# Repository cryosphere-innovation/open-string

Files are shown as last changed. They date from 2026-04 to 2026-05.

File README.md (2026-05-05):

# OpenString

<!-- SPDX-License-Identifier: CC-BY-SA-4.0 -->
<!-- Copyright (c) 2026 Cryosphere Innovation (a wholly owned subsidiary of JASCO Applied Sciences). -->
<!-- Contact: Dr. Cameron Planck <cjp@cryosphereinnovation.com> -->

OpenString is the world's first open-source temperature string for environmental monitoring. It consists of a PCB design, firmware package, and assembly guide to help you bring temperature profile monitoring into any project.

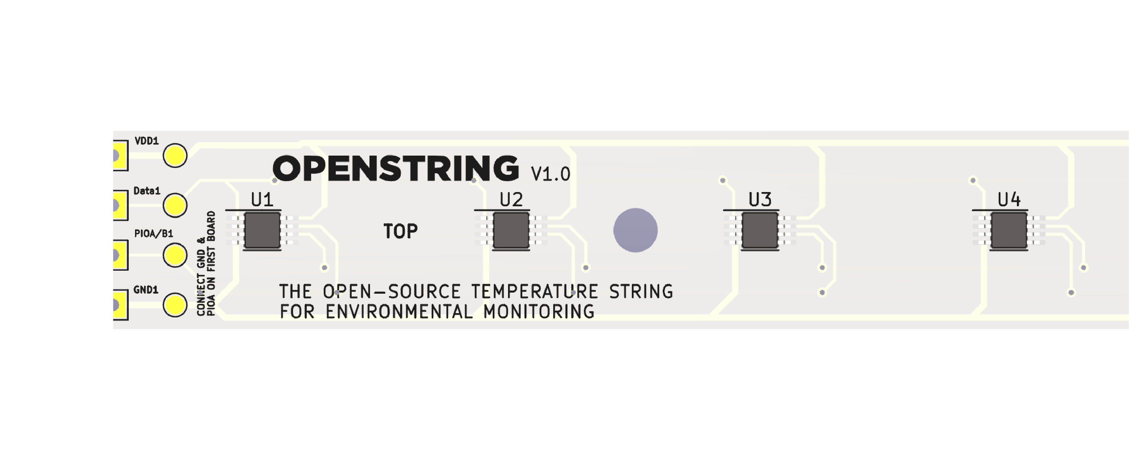
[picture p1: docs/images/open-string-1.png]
OpenString


Based on the production temperature string used by [SIMB3](https://cryosphereinnovation.com/simb3), OpenString is an extensible, arctic-hardened design that can be used as-is or tailored to your specific application. Everything you need to build, flash, and deploy one is in this repo.

> **Don't want to build your own?** Cryosphere Innovation can supply ready-to-use, assembled OpenString boards. Email [cjp@cryosphereinnovation.com](mailto:cjp@cryosphereinnovation.com) for pricing and lead time.

## Repository layout

| Path        | Contents                                                     |
| ----------- | ------------------------------------------------------------ |
| `hardware/` | KiCad project, schematic, PCB, Gerbers, BOM, fab-house notes |
| `firmware/` | Arduino sketch for the microcontroller (single `.ino` file)  |
| `docs/`     | Markdown (MDX) source rendered on the Cryosphere docs site   |
| `LICENSES/` | Full text of each license used in the project                |
| `LICENSE`   | Top-level license map                                        |

## Build your own

1. Read [`docs/ordering.mdx`](./docs/ordering.mdx) to order the PCB and parts.
2. Follow [`docs/open-string-assembly.mdx`](./docs/open-string-assembly.mdx) for the multi-step assembly walkthrough (soldering, housing, potting, testing).
3. Flash the firmware (see below, or [`docs/firmware.mdx`](./docs/firmware.mdx)).
4. Deploy.

## Hardware

The KiCad project and fabrication outputs live in `hardware/`:

- `hardware/board-files/` — KiCad project (schematic, PCB layout, project settings)
- `hardware/fabrication/gerbers/` — Gerbers and drill files ready to upload to a PCB house

See [`docs/ordering.mdx`](./docs/ordering.mdx) for the current ordering guide
(fab house settings, stencil, assembly options, expected cost).

Hardware design files are released under **CERN-OHL-S 2.0**
([`LICENSES/CERN-OHL-S-2.0.txt`](./LICENSES/CERN-OHL-S-2.0.txt)).

## Firmware

Single-file Arduino sketch at
[`firmware/src/open_string.ino`](./firmware/src/open_string.ino). PlatformIO
project config at [`platformio.ini`](./platformio.ini). Target board:
**Adafruit Feather M0** (SAMD21).

### Building with PlatformIO (recommended)

1. Install [PlatformIO Core](https://docs.platformio.org/page/core/installation.html)
   (or the PlatformIO IDE extension for VS Code).
2. From the repo root (the folder containing `platformio.ini`):
   ```sh
   pio run                  # compile
   pio run --target upload  # flash over USB
   pio device monitor       # open serial console at 115200 baud
   ```
   PlatformIO installs the SAMD board support and the OneWire library
   automatically based on `platformio.ini`.

   In VS Code, open the repo root as the workspace folder so the
   PlatformIO extension can find `platformio.ini`.

### Building with the Arduino IDE

1. Install the [Arduino IDE](https://www.arduino.cc/en/software) (or
   `arduino-cli`) and the SAMD board support package.
2. The Arduino IDE expects the sketch folder name to match the `.ino`
   filename — rename `firmware/src/` to `firmware/open_string/` (or
   symlink it) and open `open_string.ino` from there.
3. Select **Adafruit Feather M0** as the board, pick the right port,
   and click **Upload**.

See [`docs/firmware.mdx`](./docs/firmware.mdx) for the full flashing
guide, including fuse settings and troubleshooting.

Firmware source is released under **GPL-3.0**
([`LICENSES/GPL-3.0.txt`](./LICENSES/GPL-3.0.txt)).

## License

OpenString is multi-licensed. See [`LICENSE`](./LICENSE) for the full map.
Summary:

- **Hardware** — CERN-OHL-S 2.0
- **Firmware** — GPL-3.0
- **Documentation** — CC-BY-SA-4.0

All three allow commercial use and require attribution. Derivative works
must remain open under the same license.

## How the docs are published

The OpenString documentation lives at
[cryosphereinnovation.com/docs](https://cryosphereinnovation.com/docs).
The live site bakes the MDX files in `docs/` into its build output
when it deploys, so changes here go live the next time the docs site
rebuilds.

`docs/manifest.json` is generated automatically by a GitHub Action
(`.github/workflows/manifest.yml`) on every push that touches an MDX
file. You don't need to edit it by hand — just add/edit `.mdx` files
and push.

## Contributing

Issues and pull requests welcome. By contributing, you agree to license
your contribution under the license that applies to the directory you
are contributing to (see [`LICENSE`](./LICENSE)).

## Maintainer and contact

OpenString is maintained by **Cryosphere Innovation** (a wholly owned
subsidiary of JASCO Applied Sciences). Primary contact:
**Dr. Cameron Planck** — <cjp@cryosphereinnovation.com>.

Contributors are listed in [`AUTHORS.md`](./AUTHORS.md).

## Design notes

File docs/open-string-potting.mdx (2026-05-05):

---
title: Potting
slug: open-string-potting
type: Doc
status: Published
category: Open Source
heading: 'Prepare the work surface and seal the string with marine epoxy.'
published_date: '2026-04-29'
updated_date: ''
image: ''
image_attribution: ''
---

<VideoPlayer muxPlaybackId="028gjFW8vpOAKg1G2nBoBq5g5H2slu00OKFVZieUMml6A" />

Potting OpenString involves sealing the assembly with a waterproof compound to protect it from moisture and physical damage. The method described here uses West Marine 105 Epoxy and 207-SB Special Clear Hardener, which are readily-available marine-grade products designed for underwater use.

<Alert variant="success" className="my-6">
  <AlertDescription>
    If you are new to building OpenString assemblies, it is highly recommended to test your string electrically before potting. See [Testing & Mount](/docs/open-string-testing) for details.
  </AlertDescription>
</Alert>

## Parts, Materials, and Tools Needed

- [x] Sturdy bench, ideally at least 6 ft long
- [x] Bubble level
- [x] Brown painters paper
- [x] Masking tape
- [x] [West System 105-B Epoxy Resin](https://www.westmarine.com/west-system-105-b-epoxy-resin-318352.html)
- [x] [West System 207-SB Special Clear Hardener](https://www.westmarine.com/west-system-207-sb-special-clear-hardener-372920.html)
- [x] [White dye](https://www.amazon.com/dp/B007X4AIN0)
- [x] Popsicle stir sticks
- [x] String assemblies, ready for potting
- [x] Nitrile gloves
- [x] Trigger torch

## Prepare the Potting Surface

A clean, **level** surface is essential for successful potting. Even a small tilt will cause the potting compound to flow toward one end, changing the thickness over the sensors (and therefore their thermal response). It can also cause the compound to overflow and bond the string to the bench.

### Verify the Bench Is Level

Check X and Y level using the bubble level. If the bench is unlevel or unstable, adjust it.

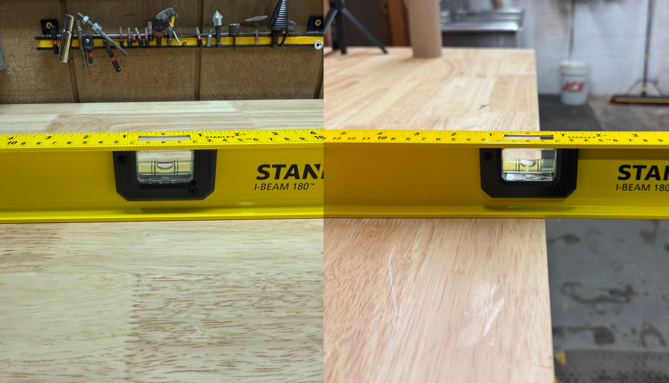
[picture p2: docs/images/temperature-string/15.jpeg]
Verify bench level A perfectly level surface is critical for potting. Even a slight tilt will cause the compound to flow toward one end and ruin the string.


### Wrap the Surface with Painters Paper

With the bench level, wrap the surface with brown painters paper and secure it with masking tape. **Wrap and secure the ends** so the paper can't bunch up — bunching can cause strings to rise and pot unevenly.

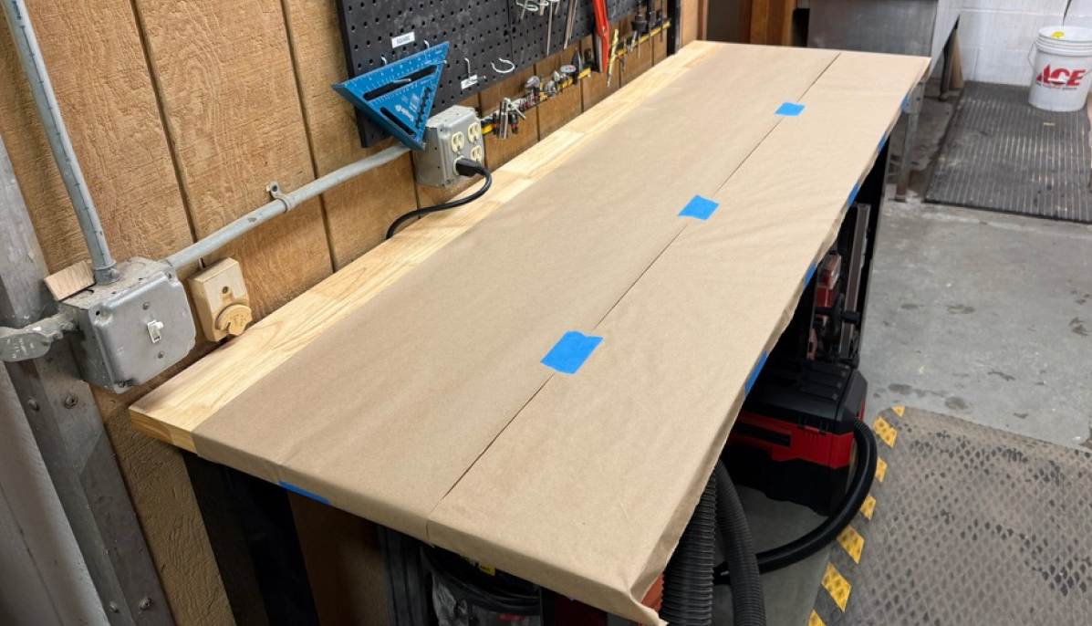
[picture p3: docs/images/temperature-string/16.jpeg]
Painters paper laid down The paper catches drips and lets you remove cured compound easily after potting.


### Lay Out the Strings

Place up to 6 string assemblies on the bench. Make sure each lies flat — pay extra attention to the top end, where the harness wires can entangle.

## Mix Epoxy, Hardener, and Dye

In a clear plastic cup, mix **7 pumps of epoxy** with **7 pumps of hardener**. Add white dye and stir for at least one minute. The dye doubles as a visual indicator of complete mixing.

## Pour Epoxy onto the String

Starting from your preferred end, slowly pour epoxy along the length of the assembly. Don't over-pour — refer to the video for pacing.

<Alert variant="success">
  <AlertDescription>
    When potting more than one string, start with the assembly placed farthest back on the bench. This keeps you from reaching over wet strings.
  </AlertDescription>
</Alert>

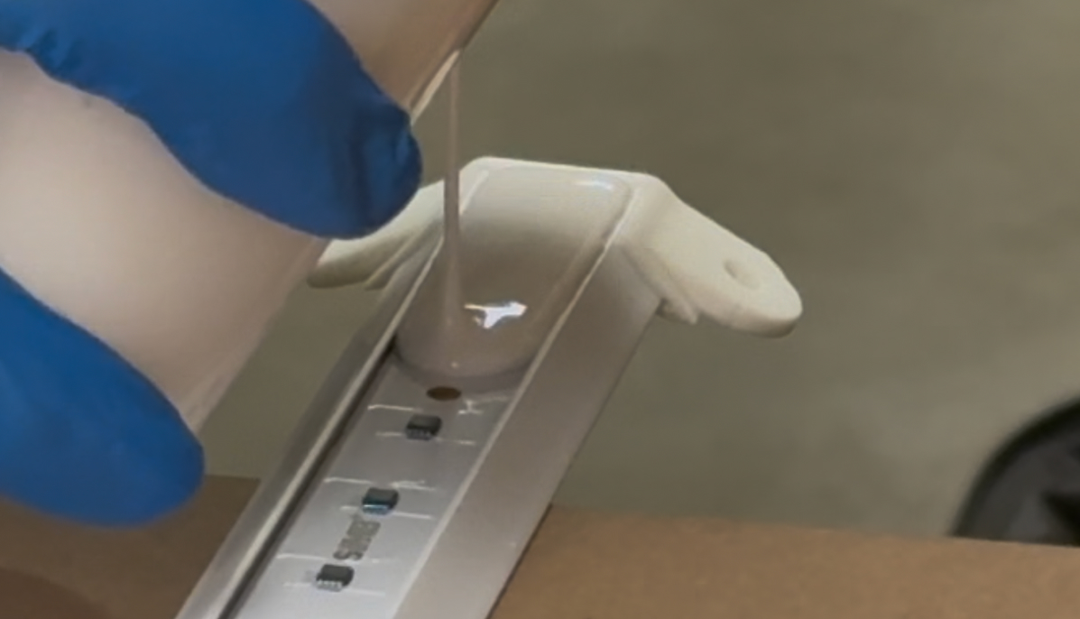
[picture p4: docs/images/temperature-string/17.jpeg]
Pouring epoxy along a string The pour pace should let the epoxy flow around the string and just touch the side of the housing.


## Remove Bubbles with a Trigger Torch

After pouring, sweep the trigger torch across the surface to pop any bubbles. Don't dwell in one spot.

## Repeat for All Strings

Pour each remaining string. You'll likely need to de-bubble each one several times during the first 1-2 hours of curing.

## Cure Time

Cure time is room-temperature dependent. The compound will gel within 30 minutes and fully cure in 24 hours. Strings can be handled after 12 hours.

<Alert variant="success">
  <AlertDescription>
    Ideal potting temperature is at least 65 °F (18 °C). If you can, turn up the heat in the room to speed curing.
  </AlertDescription>
</Alert>

After curing is complete, the strings are ready for [testing and mounting](/docs/open-string-testing).

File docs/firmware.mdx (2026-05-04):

---
title: Firmware
slug: open-string-firmware
type: Doc
status: Published
category: Open Source
heading: 'Reference Arduino sketch for reading an OpenString chain.'
published_date: '2026-04-24'
updated_date: ''
image: ''
image_attribution: ''
---

The OpenString firmware is a single Arduino sketch that reads the DS28EA00 sensors in sequence and prints each reading over serial in physical cable order. It's designed as a starting point you can adapt into your own sketch or firmware.

The source lives in [`firmware/src/open_string.ino`](https://github.com/cryosphere-innovation/open-string/blob/main/firmware/src/open_string.ino). It's heavily commented; if you're porting to another platform, the inline notes are the canonical reference.

## What the Sketch Does

On boot, the sketch walks the chain in **chain mode**, which allows the firmware to discover each chip's 64-bit ROM address in physical cable order. Once discovered, the main loop kicks off a `Convert T` on every chip simultaneously, then reads each scratchpad in order and prints the temperature.

## Hardware Requirements

OpenString needs three things from the host microcontroller:

- A **3.3 V GPIO** for the 1-Wire data line
- A **3.3 V supply** and shared ground
- A **4.7 kΩ pull-up resistor** between the data line and 3.3 V

The 1-Wire protocol supports parasitic power, but we don't recommend it for OpenString — 20+ chips drawing simultaneously during `Convert T` produces inconsistent results. Use a dedicated 3.3 V supply from your board or external power supply.

The sketch is verified on an Adafruit Feather M0 but should run on any Arduino-compatible board with a free GPIO.

## Setup

The firmware is set up as a [PlatformIO](https://platformio.org/) project (`platformio.ini` in the repo root), but the sketch also runs directly in the Arduino IDE if you prefer. Either path needs the same single dependency: the `OneWire` library.

### Option A: PlatformIO (recommended)

1. Install [PlatformIO](https://platformio.org/install) — the VS Code extension is the easiest path.
2. Clone the repository and open the `open-string` folder.
3. Build and upload:

```bash
pio run -t upload
```

PlatformIO reads `platformio.ini`, installs `OneWire` automatically, and flashes the configured board (default: `adafruit_feather_m0`). To target a different board, edit the `[env:...]` block in `platformio.ini` — see [PlatformIO's board list](https://docs.platformio.org/en/latest/boards/) for IDs.

### Option B: Arduino IDE

1. Install the [Arduino IDE](https://www.arduino.cc/en/software) (2.x recommended).
2. Install the board support package for your target (e.g. *Arduino SAMD Boards* for the Feather M0).
3. Install the `OneWire` library via **Sketch → Include Library → Manage Libraries…**.
4. Open `firmware/src/open_string.ino`, select your board and port, and click **Upload**.

## Configuration

The tunable constants live at the top of `open_string.ino`:

| Constant | Default | What it controls |
|---|---|---|
| `DATA_PIN` | `2` | GPIO connected to the 1-Wire data line |
| `MAX_SENSORS` | `40` | Maximum sensors expected on one string (8 bytes of RAM each) |
| `CONVERT_T_MS` | `750` | 12-bit Convert T worst case from the DS28EA00 datasheet |
| `INTERVAL_MS` | `10000` | Time between completed read cycles |

For most uses, only `DATA_PIN` and `INTERVAL_MS` need touching.

## Expected Output

After flashing, open the serial monitor at **115200 baud**. You should see something like:

```
=== OpenString firmware ===
Data pin: D2

Discovered 20 sensor(s) in physical cable order:
  1: [42 11 22 33 44 55 66 AB]
  2: [42 11 22 33 44 55 66 CD]
  ...

--- t=823 ms ---
  1: 18.31 C
  2: 18.00 C
  3: 17.75 C
  ...
```

If discovery returns 0 sensors, check the pull-up resistor and the harness wiring (red→VDD, black→GND, white→data).

## Porting to Other Platforms

The sketch is structured so the chain-mode discovery and per-chip read sequences map cleanly to any 1-Wire master. If you're moving to ESP-IDF, MicroPython, Zephyr, or a bare-metal driver, the byte sequences (`CHAIN ON`, `CONDITIONAL READ ROM`, `CHAIN DONE`, `Convert T`, `Match ROM`, `Read Scratchpad`) are the same — only the surrounding I/O changes. The inline comments in `open_string.ino` walk through the protocol step by step.

<Alert variant="info">
  <AlertDescription>
    The firmware is intentionally minimal — no RTC, no SD logging, no power management. We leave those choices to your application. If you build something useful on top of it, contributions back to the repository are welcome.
  </AlertDescription>
</Alert>

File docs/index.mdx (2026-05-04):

---
title: OpenString
slug: open-string-introduction
type: Doc
status: Published
category: Open Source
heading: The open-source temperature string for environmental monitoring
published_date: '2026-04-24'
updated_date: ''
image: ''
image_attribution: ''
---

OpenString is the world's first open-source temperature string for environmental monitoring. It consists of a PCB design, firmware package, and assembly guide to help you bring temperature profile monitoring into any project. 

Based on the production temperature string used by [SIMB3](/simb3), OpenString is an extensible, arctic-hardened design that can be used as-is or tailored to your specific application.

OpenString

Along with this documentation, the [OpenString repository](https://github.com/cryosphere-innovation/open-string) contains the version-controlled design files for the hardware, firmware, and documentation. The [licenses](/docs/open-string-licenses) permit commercial use and adaptation, provided you preserve attribution and share modifications under the same terms.

## Getting Started

OpenString is designed to be accessible to anyone with basic electronics experience. It consists of three main components:

1. **The PCB**: a 40 cm × 1.6 cm PCB populated with 20 temperature sensors at 2 cm spacing. The PCB has castellated edges at both ends so multiple boards can be soldered end-to-end into a continuous string of any length.

2. **Sample Firmware**: code that demonstrates how to interact with the hardware, including reading the sensor bus and logging the temperatures. The firmware provided is in Arduino, but can be adapted to any language you prefer.

3. **Environmental packaging** — recommendations for sealing, potting, cabling, and packaging the string for your deployment. Hardening depends on your application, so we provide guidelines and examples rather than a one-size-fits-all solution.

## Why Open-Source? 

Temperature strings are hard. They are delicate, expensive, and temperamental. Over the years, we've developed a series of solutions for SIMB3 that have proven themselves in arctic conditions. Rather than gatekeep this knowledge, we've decided to share it with the community with the hope that it starts a conversation and moves the field forward.

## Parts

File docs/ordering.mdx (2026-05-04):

---
title: Hardware & Fabrication
slug: open-string-hardware-fabrication
type: Doc
status: Published
category: Open Source
heading: How to order the OpenString PCB, parts, and cable
published_date: '2026-04-24'
updated_date: ''
image: ''
image_attribution: ''
---

Ordering OpenString PCBs requires having a PCB fabrication house produce the boards from the provided design files, and sourcing the components for assembly. Below are guidelines and recommendations for both steps.

A complete set of fabrication files is provided at [`hardware/fabrication/gerbers/`](https://github.com/cryosphere-innovation/open-string/tree/main/hardware/fabrication/gerbers): Gerber files for all copper, soldermask, and silkscreen layers, edge cuts, drill files (PTH and NPTH), and a `.gbrjob` manifest. Most fab houses accept the folder as a zipped upload.

<Alert variant="success" className="my-6">
  <AlertDescription>
    If you'd rather skip fabrication and assembly, Cryosphere Innovation can supply ready-to-use OpenString boards. Email [cjp@cryosphereinnovation.com](mailto:cjp@cryosphereinnovation.com) for pricing and lead time.
  </AlertDescription>
</Alert>

## Fabrication Considerations

### 40 cm length

The OpenString PCB is 40 cm × 1.6 cm. That length sits at or beyond the maximum board dimension for most fabs' standard instant-quote tiers, so you may need to request a manual quote instead. Below you'll find two suppliers that have successfully produced OpenString PCBs: MacroFab and PCBWay. If ordering from another vendor, you'll want to confirm that they can accommodate the extended length.
### Castellated edges

The PCB has castellated through-holes at both ends so boards can be soldered end-to-end into a continuous string. This is a feature you'll likely need to request explicitly. Most fabs support it but treat it as an extra-cost option.

### Recommended fab houses

- **[MacroFab](https://www.macrofab.com/)** — US-based, full turnkey manufacturing and assembly. Best if you want a single vendor handling boards, parts sourcing, and pick-and-place.
- **[PCBWay](https://www.pcbway.com/)** — China-based, fast and inexpensive for bare boards, with optional assembly service. Good default for prototype runs.

## 2. Bill of materials

The canonical BOM used for PCBA is [`hardware/fabrication/bom.xlsx`](https://github.com/cryosphere-innovation/open-string/blob/main/hardware/fabrication/bom.xlsx). There is only one line item: the [DS28EA00 temperature sensor](https://www.analog.com/media/en/technical-documentation/data-sheets/ds28ea00.pdf). Each OpenString PCB requires 20 DS28EA00s, which are spaced at 2 cm intervals along the board.

DS28EA00 chips are a cousin of the ubiquitous DS18B20, but with an extra GPIO that allows them to discover their position on a bus. This enables OpenString to read chips in a known order, enabling sequential temperature detection.

Most parts are available from Digi-Key, Mouser, Newark, or any other authorized vendor. 

## Other components

- Soldering equipment and basic electronic hand tools
- Hook up wire
- A computer with the Arduino IDE (and/or PlatformIO) installed
- Sealing / potting supplies appropriate to your deployment

Recommended:
- An Arduino Uno or similar microcontroller for testing and development. In this example, we use an [Adafruit Feather M0](https://www.adafruit.com/product/3857)

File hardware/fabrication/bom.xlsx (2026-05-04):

 |  |  | xxxx xxxx xxxxx xxPCS BOM (Sample Bill of Materials)
Item # | *Designator | *Qty | Manufacturer | *Mfg Part # | Description / Value | *Package/Footprint | Type | Your Instructions / Notes
1 | U1-U20 | 20 | Analog Devices/Maxim Integrated | DS28EA00U/ DS28EA00U+T&R | DIGITAL TEMPERATURE SENSOR | 8-TSSOP, 8-MSOP | SMD | 20 PER BOARD, THIS IS THE ONLY SMD COMPONENT
Need a quick and accurante quote? Need an efficient production? Please read SMT Ordering Necessary Files & Info in 1 minute. Thank you very much! (https://www.pcbway.com/smt_ordering_guide.html)
Click for Instructions on How to Create a BOM (https://www.pcbway.com/blog/PCB_Assembly/How_to_Build_a_BOM__Bill_Of_Materials_.html)

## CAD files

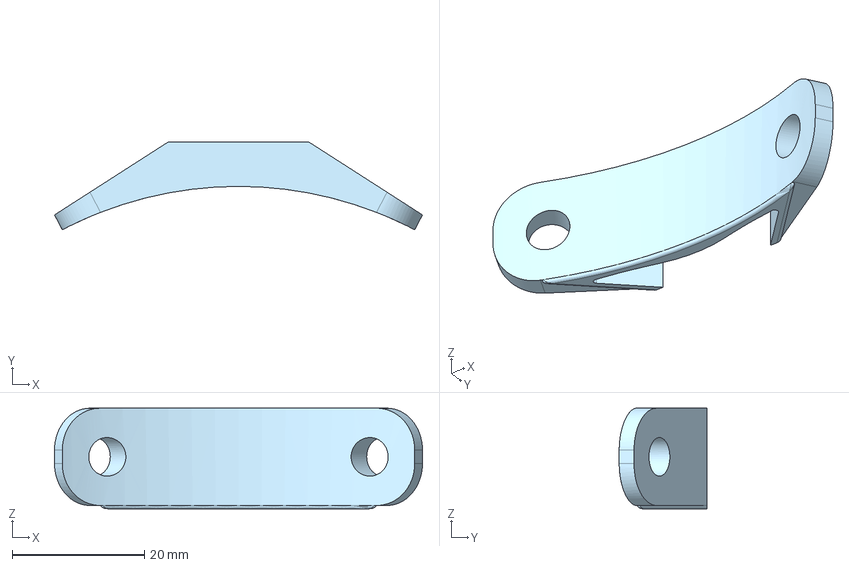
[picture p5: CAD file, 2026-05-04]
hardware/solid-files/open-string-center-end.step
55.7 x 13.3 x 15.2 mm

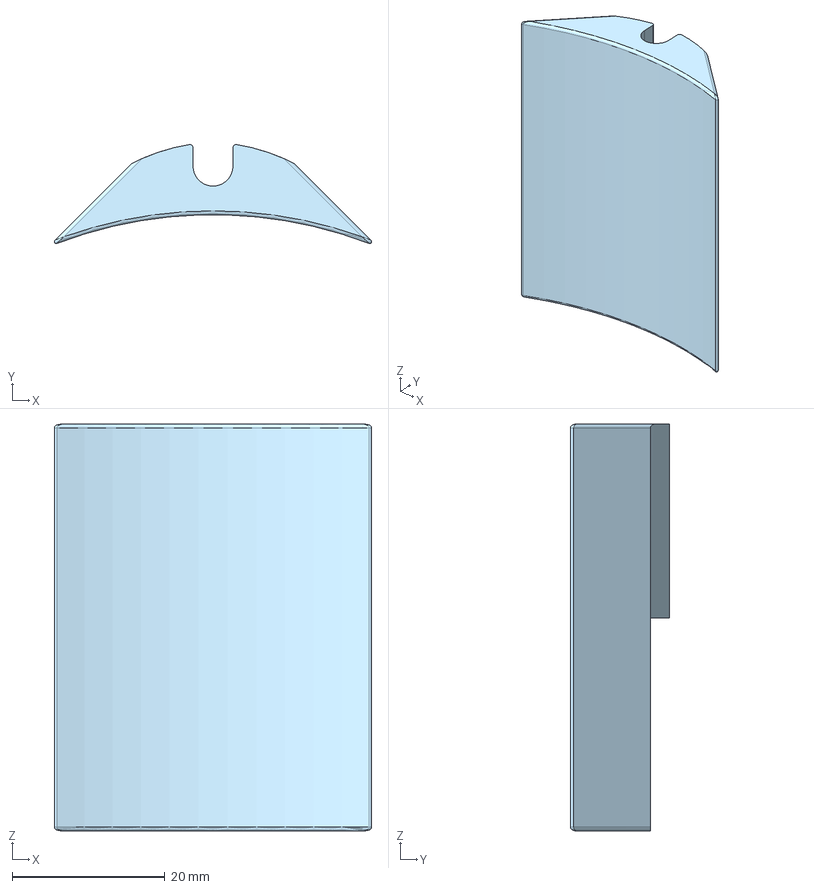
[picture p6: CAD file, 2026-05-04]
hardware/solid-files/open-string-top-end.step
41.6 x 13.0 x 53.3 mm

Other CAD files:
hardware/solid-files/open-string-extrusion.DXF
hardware/solid-files/open-string-center-end.stl
hardware/solid-files/open-string-top-end.stl

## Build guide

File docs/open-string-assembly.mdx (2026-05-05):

---
title: Assembly Overview
slug: open-string-assembly
type: Doc
status: Published
category: Open Source
heading: 'How OpenString boards are soldered, packaged, and validated into a finished string.'
published_date: '2026-04-29'
updated_date: ''
image: ''
image_attribution: ''
---

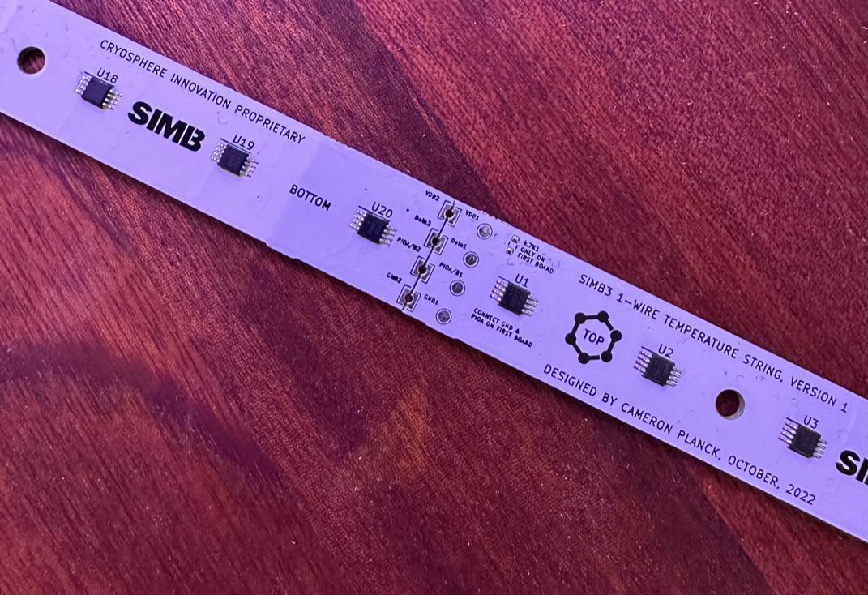
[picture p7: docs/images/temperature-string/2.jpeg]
OpenString PCB


After PCBA, OpenString is assembled by soldering the PCBs end-to-end and attaching the 3-wire harness. You can solder together as many boards as you like to create a string of any length. The assembly is then packaged for installation by potting in a protective housing.

## Assembly Steps

The pages in this section walk through the full assembly workflow:

1. [Solder Boards](/docs/open-string-assembly-solder): connect PCBs end-to-end and attach the 3-wire harness.
2. [Prepare Housing](/docs/open-string-assembly-housing): an example housing approach using extruded plastic and 3D-printed end caps.
3. [Potting](/docs/open-string-potting): prep the work surface and seal the assembly with marine epoxy.
4. [Testing & Mount](/docs/open-string-testing): run a final electrical check and prepare string for installation.

The packaging steps (housing, potting, VHB) necessarily depend on your specific application. We describe the SIMB3 approach as one concrete example. Adapt the materials and method to your own application.

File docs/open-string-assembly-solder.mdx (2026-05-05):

---
title: Solder Boards
slug: open-string-assembly-solder
type: Doc
status: Published
category: Open Source
heading: 'Chain OpenString PCBs end-to-end and attach the 3-wire harness.'
published_date: '2026-04-29'
updated_date: ''
image: ''
image_attribution: ''
---

<VideoPlayer muxPlaybackId="VawEJmEZlZvd40089uD3V7Jfp5HgirQR00d500XuP48I7k" />

## Parts, Materials, and Tools Needed

- [x] OpenString PCBs (any number, depending on the string length you need)
- [x] Housing (see [Prepare Housing](/docs/open-string-assembly-housing) for the SIMB3 example)
- [x] 3-conductor harness cable
- [x] Hookup wire
- [x] Soldering station (iron, solder, wetted sponge, etc.)
- [x] Box knife
- [x] Safety glasses, nitrile gloves

## Insert PCBs and Solder Together

Place the OpenString PCBs into the housing in the order they will sit in the finished string. Pay attention to orientation: the **bottom** of one board connects to the **top** of the next.

Connect the boards electrically by soldering each of the 4 castellated holes between adjacent boards. Reference the video for a visual guide.

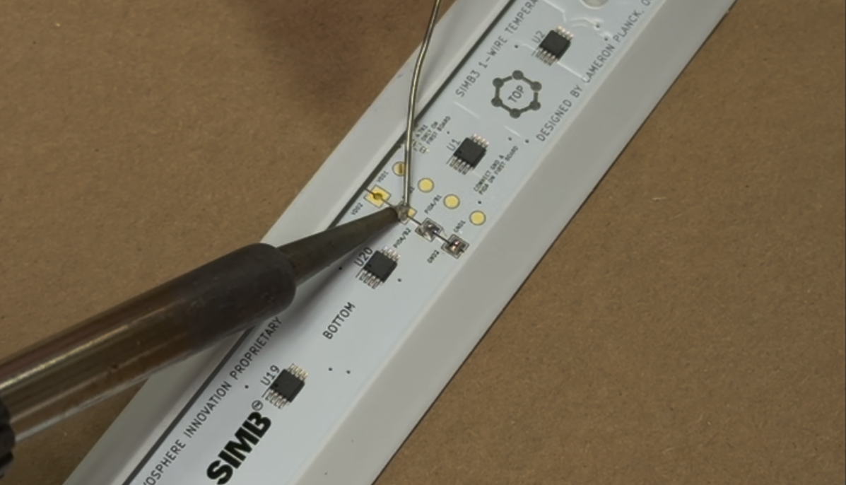
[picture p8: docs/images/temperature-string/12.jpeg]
Soldering castellated joints Each of the 4 castellated holes between adjacent boards should be soldered together to form a continuous measurement path.


Make sure each castellated hole is soldered thoroughly, but be careful not to overheat the joint.

<Alert variant="success">
  <AlertDescription>
    When joining two boards, solder one castellated hole first. You can then reheat the joint to reposition the boards squarely before soldering the rest.
  </AlertDescription>
</Alert>

## Prepare the Harness Cable

The harness cable connects the string to your data logger or microcontroller.

1. Cut a section of harness cable to your desired length. For SIMB3, we cut it to 28 inches. 
2. Using a box knife, strip the outer insulation to leave an exposed section of insulated cable. The majority of the outer jacket should be removed.
3. Cut away the **green** wire, leaving only the red, black, and white conductors.
4. Strip the ends of the red, black, and white wires **1/4 inch**.
5. Tin each end. Leave a small ball of solder — it makes connecting the harness to the PCB easier later.

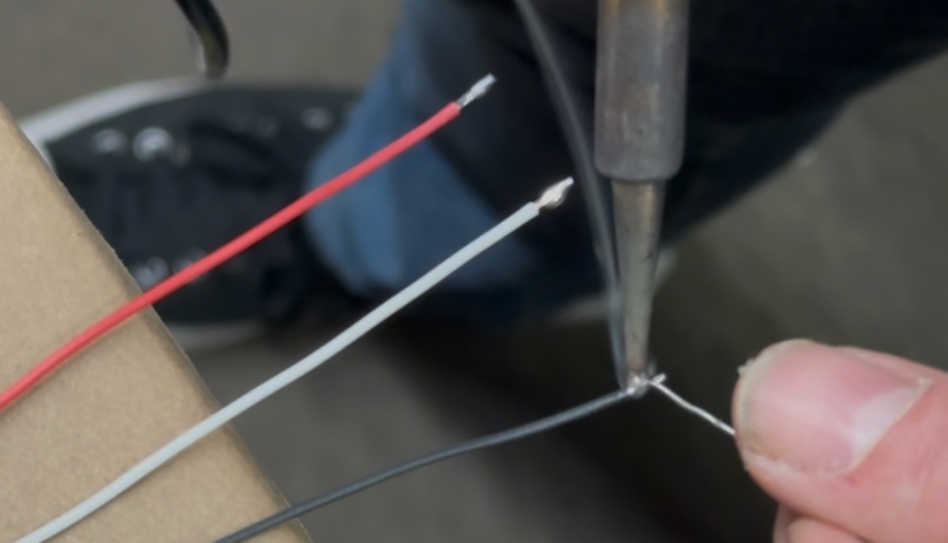
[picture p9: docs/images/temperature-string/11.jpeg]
Tinning harness wires When tinning the three wires, leave a nice ball of solder. It makes the next step easier.


## Insert Harness into Housing

Gently insert the harness through the hole in the top end of the housing. Only the insulated section should be exposed outside the housing.

## Solder the Harness to the Top PCB

Solder the three wires to the top PCB:

- **Red** → **VDD** castellated hole
- **Black** → **GND1** castellated hole
- **White** → **Data1** castellated hole

### Ground PIOA/B on the Top PCB

Using a stripped, tinned piece of hookup wire, connect the **PIOA/B** pad to the **GND1** pad on the top PCB. This is required for the chain's sequence-detection feature, which lets the firmware determine the position of each sensor at run-time.

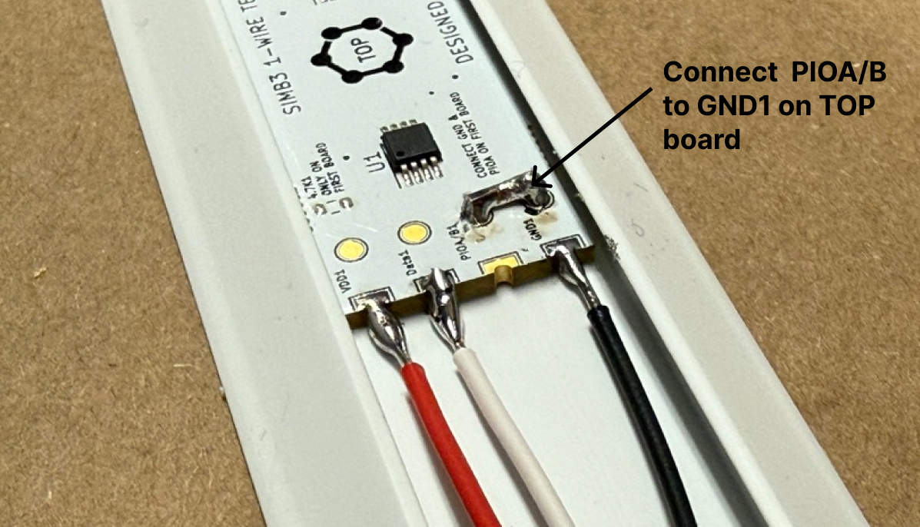
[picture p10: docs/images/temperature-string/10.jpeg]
Harness connected to top PCB with PIOA/B grounded Solder each of the three harness wires to the top PCB. Keep the wires flat and straight so they sit beneath the potting compound. For the PIOA/B → GND jumper, leaving a longer (1/2 inch) piece of hookup wire makes positioning easier.


## Super Glue the Harness Wires to the Housing

1. Position the string and harness so the bottom edge of the first PCB is touching the bottom end of the housing. Place a dab of super glue on the bottom edge to hold it in place.

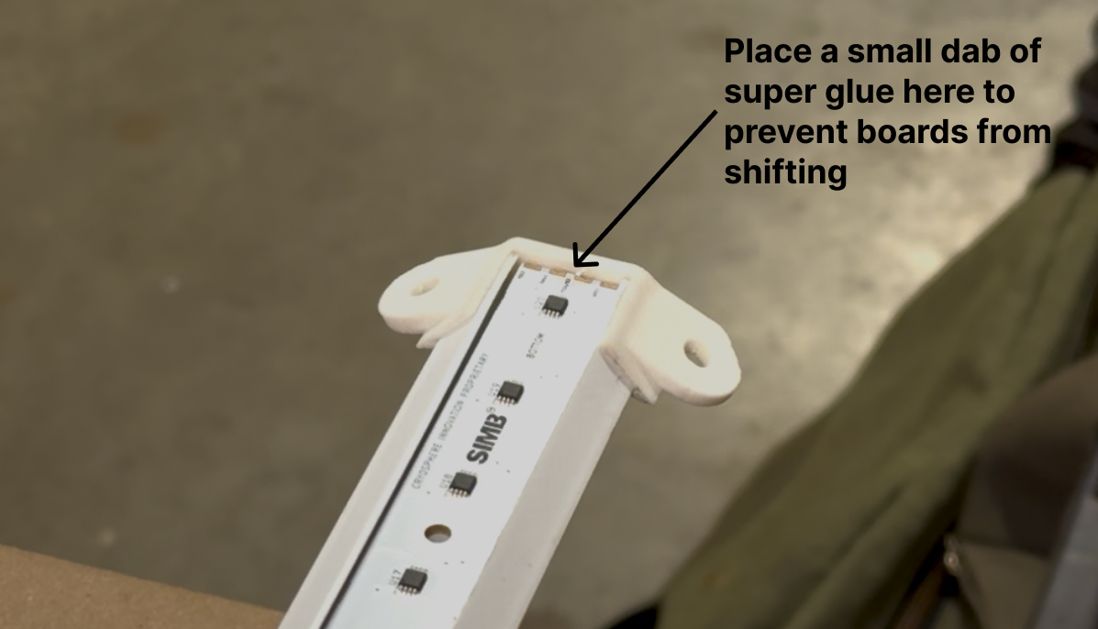
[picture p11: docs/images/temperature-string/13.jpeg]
Bottom PCB seated against housing end If the bottom PCB isn't touching the bottom end piece, the 2 cm sensor spacing relative to the housing will be off.
   

2. Starting near the top PCB, group the harness wires together and place a dab of super glue. Use accelerator to speed setting.
3. Repeat every 10 inches or wherever needed to keep the wires flat against the housing. Bulging wires will protrude through the potting compound.

## Seal the Top End with Super Glue

Apply a generous amount of super glue around the harness hole at the top end of the housing to seal it. Use accelerator to speed setting.

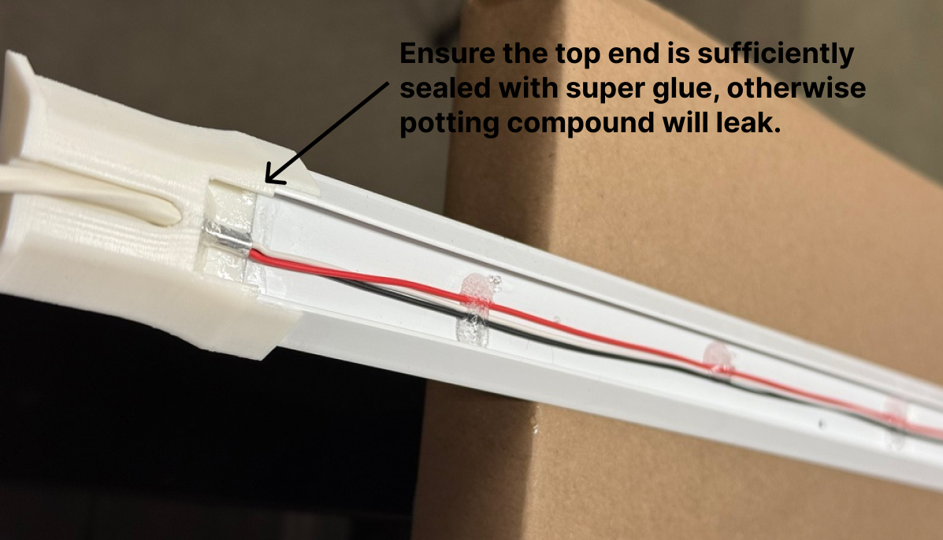
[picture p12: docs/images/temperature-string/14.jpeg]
Top end sealed with super glue Sealing the harness hole prevents potting compound from leaking out during the next step.


The string is now ready for [potting](/docs/open-string-potting), then [testing and mounting](/docs/open-string-testing).

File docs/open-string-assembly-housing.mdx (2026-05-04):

---
title: Prepare Housing
slug: open-string-assembly-housing
type: Doc
status: Published
category: Open Source
heading: 'Build the string housing by cutting an extrusion to length and gluing the end caps in place.'
published_date: '2026-04-29'
updated_date: ''
image: ''
image_attribution: ''
---

<VideoPlayer muxPlaybackId="7Vm9aAMs4bnwoH6SGdciD5QP7HzqVplbV5UiwwTLiZE" />

For most applications, OpenString PCBs will need to be secured in some kind of enclosure to protect them from the environment and allow physical mounting. 

The approach described here is the one used for SIMB3 and uses a piece of extruded plastic with 3D-printed end caps. The extrusion cradles the PCBs so they can be potted with epoxy and sealed for weather-proof use.

A DXF of the extrusion profile used for SIMB3 is [`available in the repository`](https://github.com/cryosphere-innovation/open-string/blob/main/hardware/solid-files/open-string-extrusion.DXF). You can use this file to source your own extrusion, or adapt the design to your needs. It is designed to be mounted externally using VHB tape to 4 inch diameter SCH 40 plumbing pipe.

We've also provided solid files for the top and center end caps used to seal the extrusion for potting — see the parts list below.

## Parts, Materials, and Tools Needed

- [x] Plastic extrusion of desired length
- [x] [`3D-printed top end cap`](https://github.com/cryosphere-innovation/open-string/blob/main/hardware/solid-files/open-string-top-end.stl)
- [x] [`3D-printed center end cap`](https://github.com/cryosphere-innovation/open-string/blob/main/hardware/solid-files/open-string-center-end.stl) 
- [x] Miter saw
- [x] Thick super glue + accelerator
- [x] Q-tips
- [x] Safety glasses, nitrile gloves, and ear protection

## Cut Extrusion to Length

Cut or assemble the extrusion to your target length. For reference: SIMB3 uses **78.5 inches**, which fits four PCBs (an 80-sensor string).

## Add the Top End Cap

Spread a layer of super glue into the recesses of the top end cap and slide it onto one end of the extrusion. Coat the corners thoroughly — that's where potting compound is most likely to leak out later.

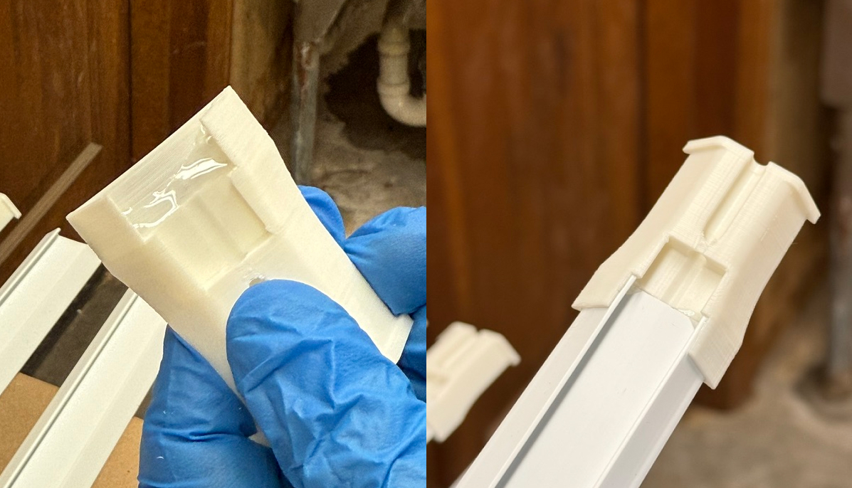
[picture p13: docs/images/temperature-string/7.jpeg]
Top end glued and set Left: top end cap freshly prepared with super glue. Right: top end cap fully set and bonded to the extrusion.


## Add the Center End Cap

Repeat for the center end cap. If glue pools at the bottom, remove or spread the excess with a Q-tip.

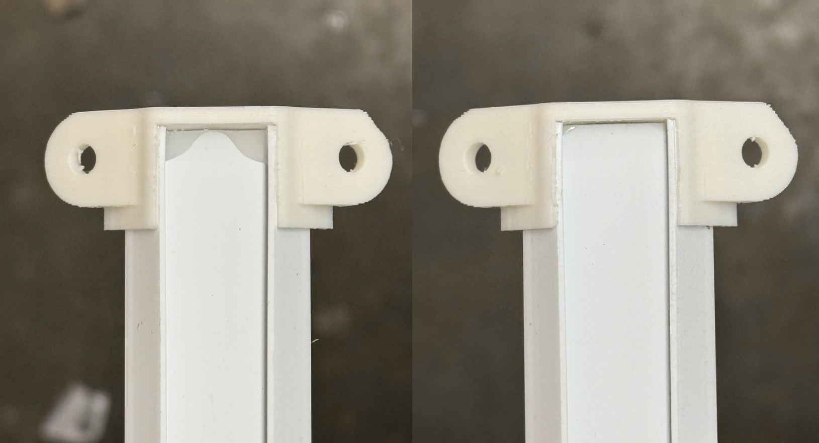
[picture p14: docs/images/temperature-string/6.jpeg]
Center end glue cleanup Note the buildup of super glue in the left picture. It must be removed or spread out so it doesn't interfere with seating the PCBs.


## Seal the Backside

Flip the housing and apply a thin layer of super glue with a Q-tip along the seam between the extrusion and each end cap. Seal all visible gaps. Reference the video for technique.

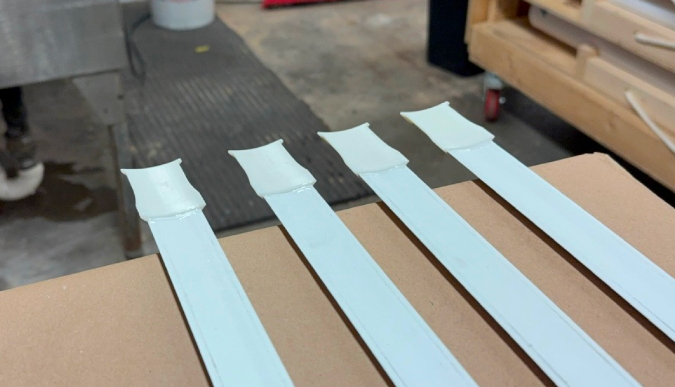
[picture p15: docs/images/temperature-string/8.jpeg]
Backside seam sealed The layer should be thick enough to seal visible gaps but thin enough not to protrude past the back surface of the housing.


## Seal the Inner Side of the Top End

Flip the housing upright and apply another thin layer of super glue along the inner side of the top end.

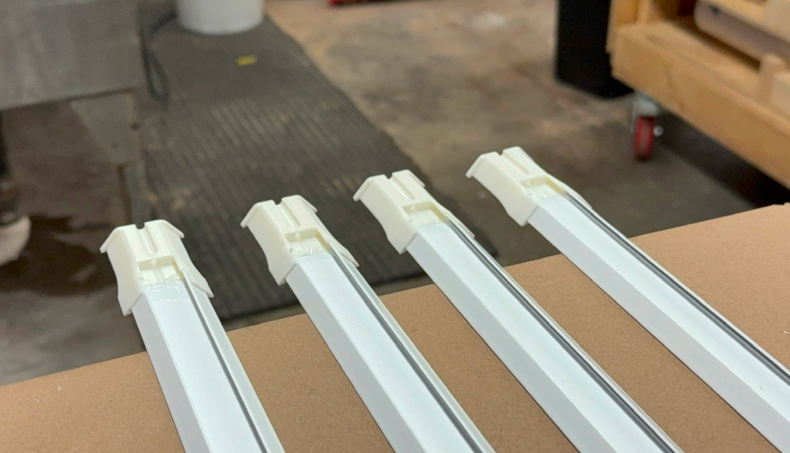
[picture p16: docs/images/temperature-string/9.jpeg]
Inner top end sealed


The housing is now ready for [board insertion and soldering](/docs/open-string-assembly-solder).

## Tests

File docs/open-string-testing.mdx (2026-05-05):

---
title: Testing & Mount
slug: open-string-testing
type: Doc
status: Published
category: Open Source
heading: 'Verify PCB operation and add VHB tape for mounting.'
published_date: '2026-04-29'
updated_date: ''
image: ''
image_attribution: ''
---

<VideoPlayer muxPlaybackId="SYM8005plFTp02sOOkeVEXdt7NTrF4x9ULIsZz6GPrclQ" />

After potting, the string should be tested to ensure the sensors are reporting correctly. Optionally and depending on your mounting needs, you can add 3M VHB tape to the back of the housing to allow for secure mounting without fasteners.

<Alert variant="success" className="my-6">
  <AlertDescription>
    The testing step can and should be performed before potting as well to verify electrical operation before sealing.
  </AlertDescription>
</Alert>

## Parts, Materials, and Tools Needed

- [x] Fully-cured string assemblies
- [x] 3M Very-High Bond (VHB) double-sided tape (optional)
- [x] Pliers (for excess epoxy cleanup)
- [x] Alligator clips
- [x] **4.7 kΩ pull-up resistor** (required — see callout below)
- [x] Arduino with [Firmware](/docs/open-string-firmware) flashed
- [x] Computer with a serial terminal (Arduino IDE, etc.)

## Validate Operation

### Prepare the Assembly for Testing

1. Strip the end of the harness ~1.5 inches to expose the wires. Clip away the outer insulation and shielding, and cut the green wire.
2. Strip the red, black, and white wires 1/4 inch.
3. Connect the string to the Arduino with alligator clips: red to 3.3V, black to GND, and white to your data GPIO. Note: the One-Wire protocol requires the data line to be pulled to the supply voltage. 

<Alert variant="warning" className="my-6">
  <AlertTitle>Pull-up resistor required</AlertTitle>
  <AlertDescription>
    The 1-Wire protocol requires a pull-up on the data line. In most cases a 4.7 kΩ resistor between the white (data) wire and the 3.3 V supply rail will work, but for long cable runs, you may need a stronger pull-up (e.g. 2.2 kΩ) to ensure the signal is clean.
  </AlertDescription>
</Alert>

### Read the Sensors

Open the serial terminal in your IDE. You may need to select a port — it will look like `/dev/cu.usbmodem1101` or similar.

With the string connected, the program will cycle through readings from every sensor in the chain. Each reading should be between **15 and 25 °C** indoors. The example output below is from an 80-sensor (4-board) string:

```ansi
------------------ BEGINNING SCAN --------------------

Number of DS28EA00 sensors detected: 80

Converted Temperatures (deg C):
Sensor 1: 18.31
Sensor 2: 18.00
Sensor 3: 17.75
.
.
.
Sensor 78: 20.94
Sensor 79: 19.00
Sensor 80: 23.25
```

If every sensor reports a sensible value, the string is ready for deployment. Label the assembly, set it aside, and repeat for the rest.

## Prepare for Mounting (optional)

### Scrape Off Excess Epoxy

Inspect the backside of each string for any leaked epoxy. Snap off any blobs with pliers. Excess epoxy will keep the string from laying flat against the bonding surface and will prevent the tape from adhering.

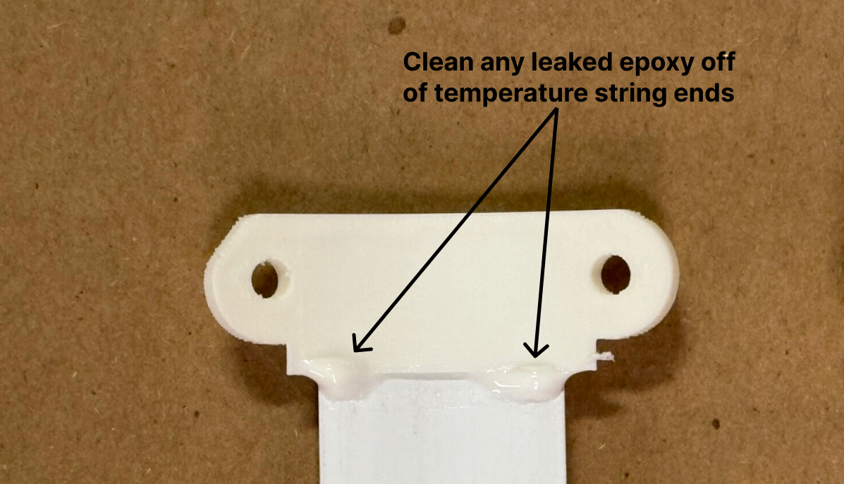
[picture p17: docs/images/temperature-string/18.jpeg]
Removing excess epoxy with pliers Epoxy commonly leaks at the corners of the housing ends. Snap any buildup off with pliers so the string lays flat against the bonding surface.


### Apply VHB Tape

Run a strip of 3M VHB tape along the entire backside length of the housing. Press it down with a paper towel or soft cloth to ensure it's fully set and free of bubbles.

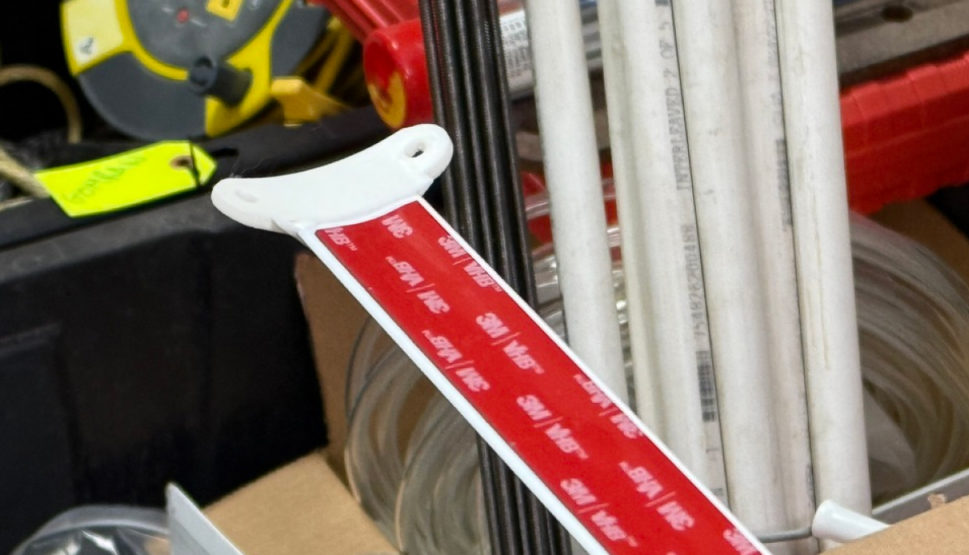
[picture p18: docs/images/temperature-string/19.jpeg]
VHB tape applied along housing backside VHB tape attaches the string to the bonding surface securely without fasteners that could compromise watertight integrity.


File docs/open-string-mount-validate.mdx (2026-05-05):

---
title: Testing & Mount
slug: open-string-mount-validate
type: Doc
status: Published
category: Open Source
heading: 'Verify PCB operation and add VHB tape for mounting.'
published_date: '2026-04-29'
updated_date: ''
image: ''
image_attribution: ''
---

<VideoPlayer muxPlaybackId="SYM8005plFTp02sOOkeVEXdt7NTrF4x9ULIsZz6GPrclQ" />

It's important to run a final check on the string after potting to verify that all sensors are reporting correctly. Optionally and depending on your mounting needs, you can add 3M VHB tape to the back of the housing to allow for secure mounting without fasteners.

## Parts, Materials, and Tools Needed

- [x] Fully-cured string assemblies
- [x] 3M Very-High Bond (VHB) double-sided tape (optional)
- [x] Pliers (for excess epoxy cleanup)
- [x] Alligator clips
- [x] Arduino with [Firmware](/docs/open-string-firmware) flashed
- [x] Computer with a serial terminal (Arduino IDE, etc.)

## Validate Operation

### Prepare the Assembly for Testing

1. Strip the end of the harness ~1.5 inches to expose the wires. Clip away the outer insulation and shielding, and cut the green wire.
2. Strip the red, black, and white wires 1/4 inch.
3. Connect the string to the Arduino with alligator clips: red to 5V, black to GND, and white to your data GPIO.

### Read the Sensors

Open the serial terminal in your IDE. You may need to select a port — it will look like `/dev/cu.usbmodem1101` or similar.

With the string connected, the program will cycle through readings from every sensor in the chain. Each reading should be between **15 and 25 °C** indoors. The example output below is from an 80-sensor (4-board) string:

```ansi
------------------ BEGINNING SCAN --------------------

Number of DS28EA00 sensors detected: 80

Converted Temperatures (deg C):
Sensor 1: 18.31
Sensor 2: 18.00
Sensor 3: 17.75
.
.
.
Sensor 78: 20.94
Sensor 79: 19.00
Sensor 80: 23.25
```

If every sensor reports a sensible value, the string is ready for deployment. Label the assembly, set it aside, and repeat for the rest.

## Prepare for Mounting (optional)

### Scrape Off Excess Epoxy

Inspect the backside of each string for any leaked epoxy. Snap off any blobs with pliers. Excess epoxy will keep the string from laying flat against the bonding surface and will prevent the tape from adhering.

Removing excess epoxy with pliers Epoxy commonly leaks at the corners of the housing ends. Snap any buildup off with pliers so the string lays flat against the bonding surface.

### Apply VHB Tape

Run a strip of 3M VHB tape along the entire backside length of the housing. Press it down with a paper towel or soft cloth to ensure it's fully set and free of bubbles.

VHB tape applied along housing backside VHB tape attaches the string to the bonding surface securely without fasteners that could compromise watertight integrity.

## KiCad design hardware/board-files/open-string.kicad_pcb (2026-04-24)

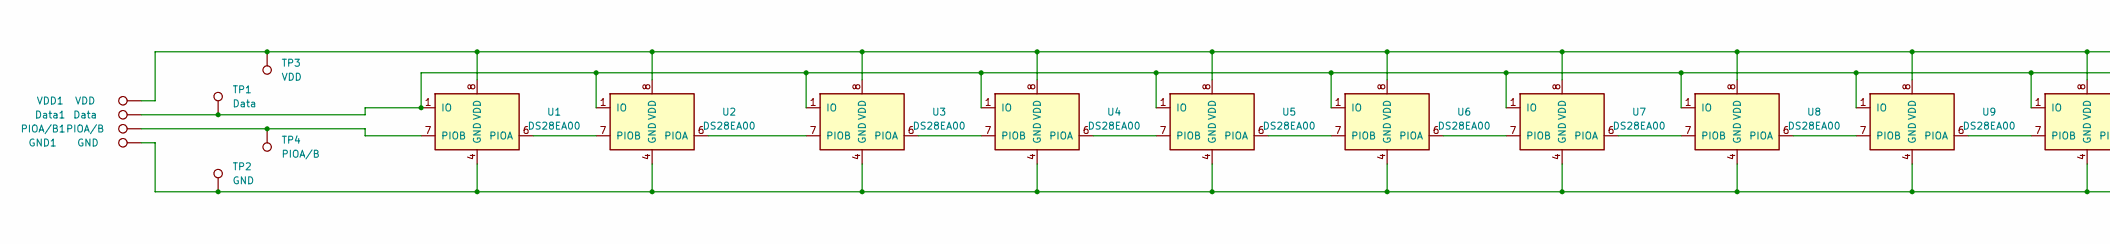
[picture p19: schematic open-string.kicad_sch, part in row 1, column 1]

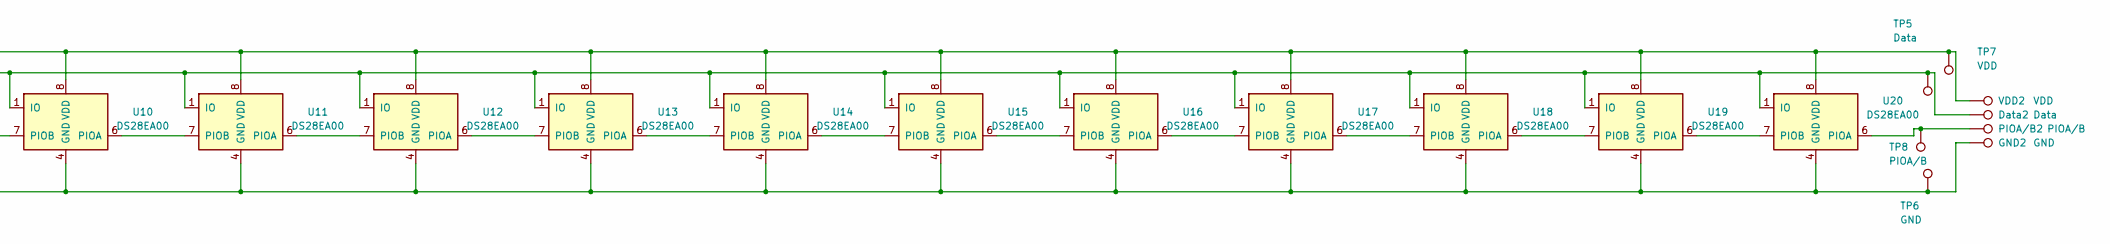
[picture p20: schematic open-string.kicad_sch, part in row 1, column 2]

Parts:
Data1, Data2: Data; TestPoint_THTPad_2.0x2.0mm_Drill1.0mm
GND1, GND2: GND; TestPoint_THTPad_2.0x2.0mm_Drill1.0mm
PIOA/B1, PIOA/B2: PIOA/B; TestPoint_THTPad_2.0x2.0mm_Drill1.0mm
TP1, TP5: Data; TestPoint_Pad_D1.5mm
TP2, TP6: GND; TestPoint_Pad_D1.5mm
TP3, TP7: VDD; TestPoint_Pad_D1.5mm
TP4, TP8: PIOA/B; TestPoint_Pad_D1.5mm
U1, U2, U3, U4, U5, U6, U7, U8, U9, U10, U11, U12, U13, U14, U15, U16, U17, U18, U19, U20: DS28EA00; MSOP-8_3x3mm_P0.65mm
VDD1, VDD2: VDD; TestPoint_THTPad_2.0x2.0mm_Drill1.0mm

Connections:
unnamed: GND1.1, GND2.1, TP2.1, TP6.1, U1.4 (GND), U2.4 (GND), U3.4 (GND), U4.4 (GND), U5.4 (GND), U6.4 (GND), U7.4 (GND), U8.4 (GND), U9.4 (GND), U10.4 (GND), U11.4 (GND), U12.4 (GND), U13.4 (GND), U14.4 (GND), U15.4 (GND), U16.4 (GND), U17.4 (GND), U18.4 (GND), U19.4 (GND), U20.4 (GND)
unnamed: Data1.1, Data2.1, TP1.1, TP5.1, U1.1 (IO), U2.1 (IO), U3.1 (IO), U4.1 (IO), U5.1 (IO), U6.1 (IO), U7.1 (IO), U8.1 (IO), U9.1 (IO), U10.1 (IO), U11.1 (IO), U12.1 (IO), U13.1 (IO), U14.1 (IO), U15.1 (IO), U16.1 (IO), U17.1 (IO), U18.1 (IO), U19.1 (IO), U20.1 (IO)
unnamed: U1.6 (PIOA), U2.7 (PIOB)
unnamed: PIOA/B1.1, TP4.1, U1.7 (PIOB)
unnamed: TP3.1, TP7.1, U1.8 (VDD), U2.8 (VDD), U3.8 (VDD), U4.8 (VDD), U5.8 (VDD), U6.8 (VDD), U7.8 (VDD), U8.8 (VDD), U9.8 (VDD), U10.8 (VDD), U11.8 (VDD), U12.8 (VDD), U13.8 (VDD), U14.8 (VDD), U15.8 (VDD), U16.8 (VDD), U17.8 (VDD), U18.8 (VDD), U19.8 (VDD), U20.8 (VDD), VDD1.1, VDD2.1
unnamed: U2.6 (PIOA), U3.7 (PIOB)
unnamed: U3.6 (PIOA), U4.7 (PIOB)
unnamed: U4.6 (PIOA), U5.7 (PIOB)
unnamed: U5.6 (PIOA), U6.7 (PIOB)
unnamed: U6.6 (PIOA), U7.7 (PIOB)
unnamed: U7.6 (PIOA), U8.7 (PIOB)
unnamed: U8.6 (PIOA), U9.7 (PIOB)
unnamed: U10.6 (PIOA), U11.7 (PIOB)
unnamed: U9.6 (PIOA), U10.7 (PIOB)
unnamed: U11.6 (PIOA), U12.7 (PIOB)
unnamed: U12.6 (PIOA), U13.7 (PIOB)
unnamed: U13.6 (PIOA), U14.7 (PIOB)
unnamed: U14.6 (PIOA), U15.7 (PIOB)
unnamed: U15.6 (PIOA), U16.7 (PIOB)
unnamed: U16.6 (PIOA), U17.7 (PIOB)
unnamed: U17.6 (PIOA), U18.7 (PIOB)
unnamed: U18.6 (PIOA), U19.7 (PIOB)
unnamed: U19.6 (PIOA), U20.7 (PIOB)
unnamed: PIOA/B2.1, TP8.1, U20.6 (PIOA)

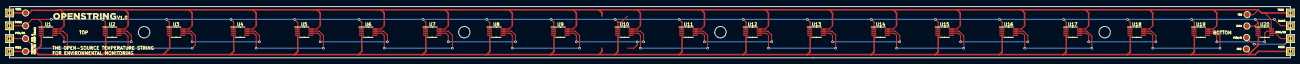
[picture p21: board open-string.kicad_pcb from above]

Board: 2 copper layers, 400.0 x 16.0 mm, 36 parts (0 on the bottom side), 24 nets.

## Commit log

2026-04-24 Initial commit: open-string hardware, firmware, and docs
    [open-string-B_Cu.gbr, open-string-B_Mask.gbr, open-string-B_Paste.gbr, open-string-B_Silkscreen.gbr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]
2026-04-24 Add docs manifest generator and GitHub Action
    The cryosphere docs site fetches this manifest at build/revalidate time
    to list available docs without hitting the GitHub API for a directory
    listing (no rate limits, one request instead of N).
    The workflow regenerates manifest.json on every push that touches an
    MDX file and auto-commits the result back to main. Path filter excludes
    manifest.json so the auto-commit doesn't re-trigger the workflow.
2026-04-24 Document how docs are published to the cryosphere site
    Clarify in the README that docs/ feeds the live cryosphere docs site via
    runtime fetch, and that manifest.json is auto-generated — contributors
    only need to edit .mdx files.
2026-04-24 Rewrite intro page with Arctic-proven track record and template framing
    Lead with the production context (three years inside SIMB3 across ~40
    Arctic/Antarctic deployments) to establish credibility, then describe
    the PCB form factor and the "template you can build on" framing before
    the license / start-here sections.
2026-04-24 Refine intro: tighten opening summary, link SIMB3 and limits page
    Restructure the lead paragraph to describe OpenString as a PCB (not a
    cable), and link the 'continuous span of any length' claim to the
    hardware reference where practical limits belong. Also link the first
    mention of SIMB3.
2026-04-24 Tighten lead paragraph, drop 'extensible platform'
    Strong first sentence (open-source, arctic-hardened, for environmental
    monitoring), then a second sentence that makes the reuse point (fork
    the whole design or take just the PCB/firmware) and closes with SIMB3
    as the proof point.
2026-05-04 Restructure docs and add SIMB3 assembly content
    Reorganize the documentation set around a multi-page assembly section
    mirroring the SIMB3 production workflow:
    - Replace the single-file assembly.mdx with five new pages: an overview
    plus Prepare Housing, Assemble Boards, Potting, and Mount & Validate.
    - Add temperature-string assembly imagery (19 photos) and Mux video IDs
    for the soldering, housing, potting, and validation walkthroughs.
    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
    [bom.xlsx, open-string-center-end.step, open-string-center-end.stl, open-string-extrusion.DXF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]
2026-05-05 Rename Mount & Validate → Testing & Mount
    Display name change in the page title, manifest, and the assembly
    overview's step list. Slug stays open-string-mount-validate so URLs
    don't break.
    The order matches the page body: electrical test first, then bond to
    the mounting surface (VHB tape).
2026-05-05 Rename mount-validate → testing slug; refresh README
    - File rename: docs/open-string-mount-validate.mdx → docs/open-string-testing.mdx
    - Frontmatter slug, manifest entry, and cross-references in
    open-string-assembly.mdx, open-string-assembly-solder.mdx, and
    open-string-potting.mdx all updated.
    README.md:
    - Lead rewritten to match the docs intro: "the world's first
    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
2026-05-05 Add pull-up resistor callout in testing doc; assembly intro tweaks
    testing.mdx:
    - Add a "Pull-up resistor required" warning callout right after the
    wiring steps. Explains the 4.7 kΩ between data and 3.3 V supply,
    with a note that long cable runs may need a stronger pull-up
    (e.g. 2.2 kΩ).
    - Add the resistor to the parts list.
    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
